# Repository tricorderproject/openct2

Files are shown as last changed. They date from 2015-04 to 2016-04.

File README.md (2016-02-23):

openct2
======

Open Source Computed Tomography (CT) Scanner v2 <br>
http://www.tricorderproject.org/openct <br>
Copyright (C) 2015  Peter Jansen and the Tricorder project <br>
peter@tricorderproject.org <br>
Project Build Logs: https://hackaday.io/project/5946-openct2 <br>

# Introduction

The Open Source Computed Tomography (CT) Scanner project aims to move towards creating an inexpensive and open desktop computed tomography scanner for academic and educational purposes.  The most common form of computed tomography is radiographic using x-rays or gamma rays, although it is my hope that this project can serve as a general platform for other kinds of tomographic research with other, safer wavelengths. 

This project is intended for use with radioisotope "check" sources that are many orders of magnitude less intense than sources in a commercial or medical radiographic setups.  This means that even very low resolution images will take hours of measurement and integration time to assemble, and the resolution and signal to noise ratio of a scan are largely a function of time (and patience).  Much of the spirit of this project is to move towards creating better scans through the use of clever signal processing techniques or wavelengths that can be more efficiently detected, rather than increasing source intensity. 

# Open Source

This project is open hardware and is released under various open licenses.  Please see LICENSES.TXT for details.

For potential contributors, a list of suggested contributions and next steps can be found in TODO.TXT .

# Warning

This project has a variety of dangers associated with it, including (without limitation) its assembly and use.  This generally includes the typical hazards involved with assembling, testing, and using electronics projects, CNC projects, as well as using hand tools, power tools, and CNC manufacturing tools such as laser cutters or CNC routers.  This is not a first project in any of these areas, and one should be well experienced and comfortable in all aspects of this project's design, assembly, and use. 

In addition, for radiography this project makes use of a low intensity sealed radioactive radioisotope source.  You should be experienced and extremely comfortable with handling and using radioactive sources, understanding the potential dangers (and how to minimize them), as well as any local laws or regulations regarding such material.  Having advanced training in medical imaging, radiography, and/or radiation biophysics is highly recommended.  

In no case should any living thing be placed inside of or be scanned by the device. 

**DISCLAIMER OF WARRANTIES AND LIMITATION OF LIABILITY.**

UNLESS OTHERWISE SEPARATELY UNDERTAKEN BY THE LICENSOR, TO THE EXTENT POSSIBLE, THE LICENSOR OFFERS THE LICENSED MATERIAL AS-IS AND AS-AVAILABLE, AND MAKES NO REPRESENTATIONS OR WARRANTIES OF ANY KIND CONCERNING THE LICENSED MATERIAL, WHETHER EXPRESS, IMPLIED, STATUTORY, OR OTHER. THIS INCLUDES, WITHOUT LIMITATION, WARRANTIES OF TITLE, MERCHANTABILITY, FITNESS FOR A PARTICULAR PURPOSE, NON-INFRINGEMENT, ABSENCE OF LATENT OR OTHER DEFECTS, ACCURACY, OR THE PRESENCE OR ABSENCE OF ERRORS, WHETHER OR NOT KNOWN OR DISCOVERABLE. WHERE DISCLAIMERS OF WARRANTIES ARE NOT ALLOWED IN FULL OR IN PART, THIS DISCLAIMER MAY NOT APPLY TO YOU.

TO THE EXTENT POSSIBLE, IN NO EVENT WILL THE LICENSOR BE LIABLE TO YOU ON ANY LEGAL THEORY (INCLUDING, WITHOUT LIMITATION, NEGLIGENCE) OR OTHERWISE FOR ANY DIRECT, SPECIAL, INDIRECT, INCIDENTAL, CONSEQUENTIAL, PUNITIVE, EXEMPLARY, OR OTHER LOSSES, COSTS, EXPENSES, OR DAMAGES ARISING OUT OF THIS PUBLIC LICENSE OR USE OF THE LICENSED MATERIAL, EVEN IF THE LICENSOR HAS BEEN ADVISED OF THE POSSIBILITY OF SUCH LOSSES, COSTS, EXPENSES, OR DAMAGES. WHERE A LIMITATION OF LIABILITY IS NOT ALLOWED IN FULL OR IN PART, THIS LIMITATION MAY NOT APPLY TO YOU.

THE DISCLAIMER OF WARRANTIES AND LIMITATION OF LIABILITY PROVIDED ABOVE SHALL BE INTERPRETED IN A MANNER THAT, TO THE EXTENT POSSIBLE, MOST CLOSELY APPROXIMATES AN ABSOLUTE DISCLAIMER AND WAIVER OF ALL LIABILITY.

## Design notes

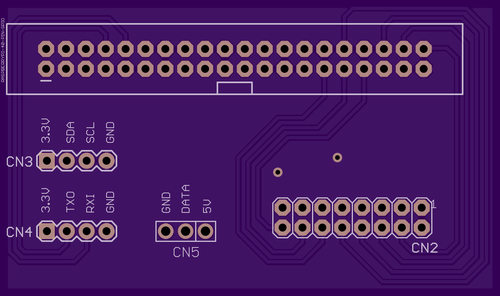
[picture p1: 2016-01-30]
hardware/navscreen/images/navscreen_piboard_rev0_top.png

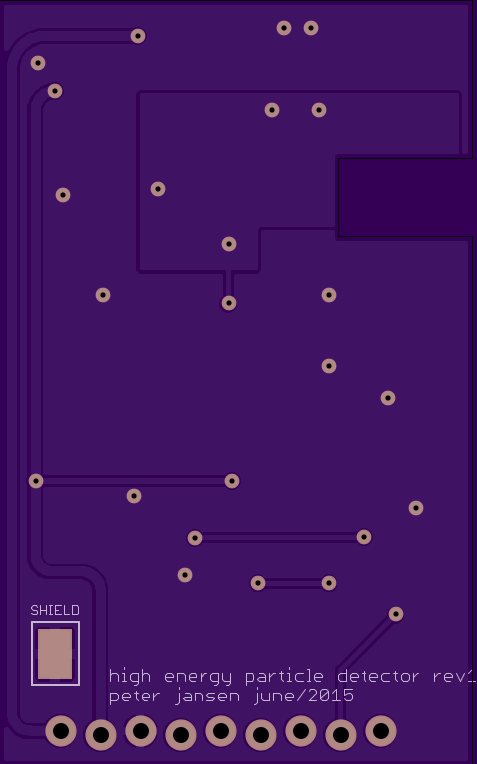
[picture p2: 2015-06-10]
hardware/radiationsensor_r1/images/radiationsensor_r1_bottom.png

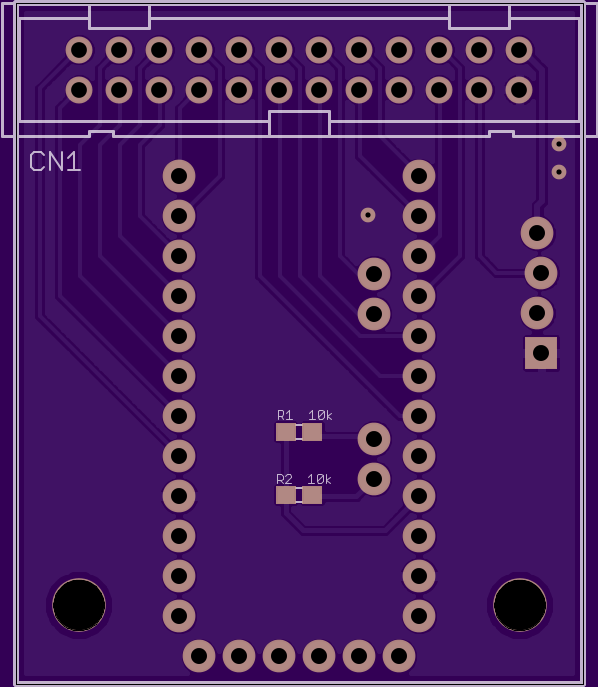
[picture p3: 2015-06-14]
hardware/radiationsensor_r1/images/microcontrollerboard_r0_top.png

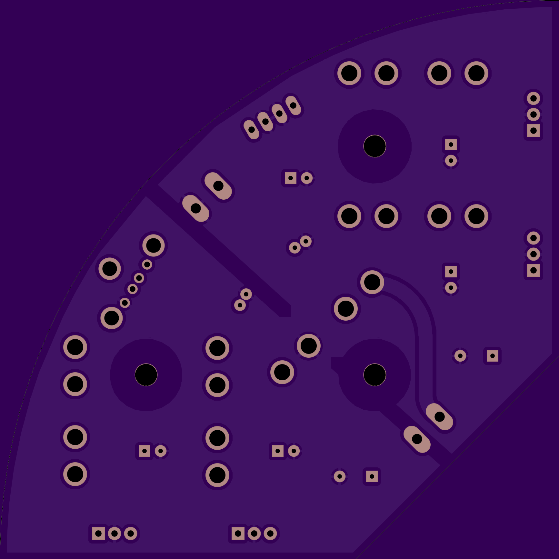
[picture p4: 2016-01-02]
hardware/powersupply/images/powersupply_r0_bottom.png

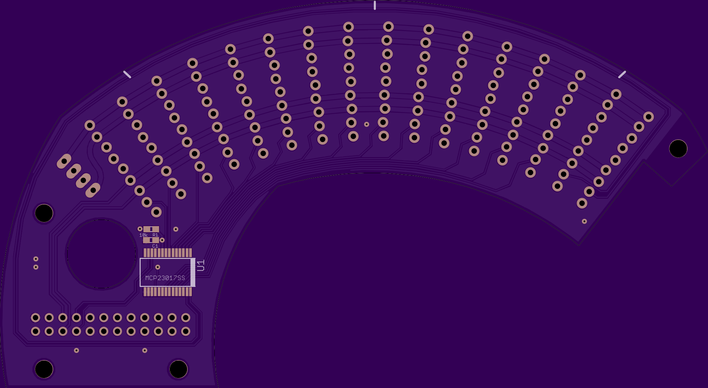
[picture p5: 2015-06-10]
hardware/radiationsensor_r1/images/arrayboard_r0_bottom.png

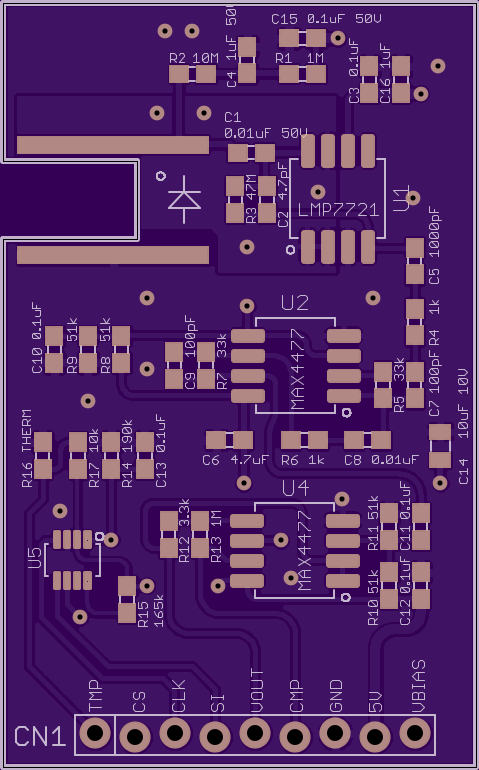
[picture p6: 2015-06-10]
hardware/radiationsensor_r1/images/radiationsensor_r1_top.png

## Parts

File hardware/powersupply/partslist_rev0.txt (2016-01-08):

CN1, CN3	JST Connector	B2B-PH-K-S(LF)(SN)
+ Cables (from Sparkfun?)

CN2		USB Connector	Molex 105057-0001		

CN4		Imaging Array Connector		A33896-ND

CN5, CN6	5mm pitch Screw Terminals			1776244-2

C3-C6		Capacitors	5mm dia, 47uF, 16V	(ECA-1EHG470)
C7		Capacitor	5mm dia, 100V		(ECA-2AM100)
C1-C2		Capacitors	10mm dia, 25V 		(ECA-1VM471)

IC1-4		2A Linear Regulators	L78S05CV-DG

F1-5		20mm/5mm Fuse Clips (qty 10)	1A3399-10

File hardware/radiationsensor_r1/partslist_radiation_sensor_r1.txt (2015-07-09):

Partlist											
											
Part	Value	Device	Package		QTY per board		# of boards		QTY total		Digikey #
											
C1	0.01uF	50V	CAP0603		1		18		18		445-16165-1-ND
"C10, *"	0.1uF	50V	603		6		18		108		311-1344-1-ND
C5	1000pF	CAP0603	603		1		18		18		445-5736-1-ND
"C7, C9"	100pF	CAP0603	603		2		18		36		1276-2159-1-ND
C14	10uF	10V	805		1		18		18		490-3886-1-ND
"C4, C16"	1uF	50V	603		2		18		36		445-7468-1-ND
C2	2.2pF	50V	603		1		18		18		399-8791-1-ND
C6	4.7uF	CAP0603	603		1		18		18		1276-1784-1-ND
											
CN1	1X09	MALE RIGHTANGLE	1X09		1		18		18		S1111EC-09-ND
											
D1	BPW34S	PHOTODIODE4STACK-SIDEMOUNT	BPW34S-4STACK-SIDEMOUNT		4		18		72		BPW34S-ND
											
R17	10k	RESISTOR0603	603		1		18		18		P10.0KHCT-ND
R2	10M	RESISTOR0603	603		1		18		18		541-10MAYCT-ND
R15	165k	RESISTOR0603	603		1		18		18		P165KHCT-ND
R14	190k	RESISTOR0603	603		1		18		18		P191KHCT-ND
"R4, R6"	1k	RESISTOR0603	603		2		18		36		P1.00KHCT-ND
"R1, R13"	1M	RESISTOR0603	603		2		18		36		P1.00MHCT-ND
R12	3.3k	RESISTOR0603	603		1		18		18		P3.30KHCT-ND
"R5, R7"	33k	RESISTOR0603	603		2		18		36		P33.0KHCT-ND
R3	47M	RESISTOR0603	603		1		18		18		541-47MAHCT-ND
"R10, R9, R10, R11"	51k	RESISTOR0603	603		4		18		72		P51.0KHCT-ND
R16	NCP18XV103	RESISTOR0603	603		1		18		18		490-6944-1-ND
											
U1	LMP7721	OPAMP-LMP7721	SOIC-8		1		18		18		LMP7721MA/NOPB-ND
"U2, U4"	MAX4477	OPAMP-MAX4477	SOIC-8		2		18		36		MAX4477ASA+-ND
U5	50k	AD5160	SOT-23-8		1		18		18		AD5160BRJZ50-RL7CT-ND
											
Other											
Stranded Wire for Ground Shield					1		1		1		CN100B-25-ND
Roll of Aluminum Tape											Hardware Store

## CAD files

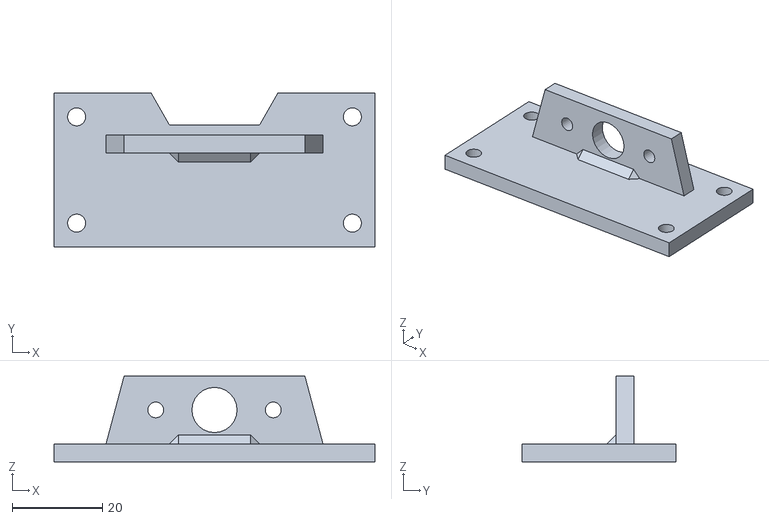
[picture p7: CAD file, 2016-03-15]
mechanical/structure/shield_mount1a_fixed.stl
71.0 x 34.0 x 19.0

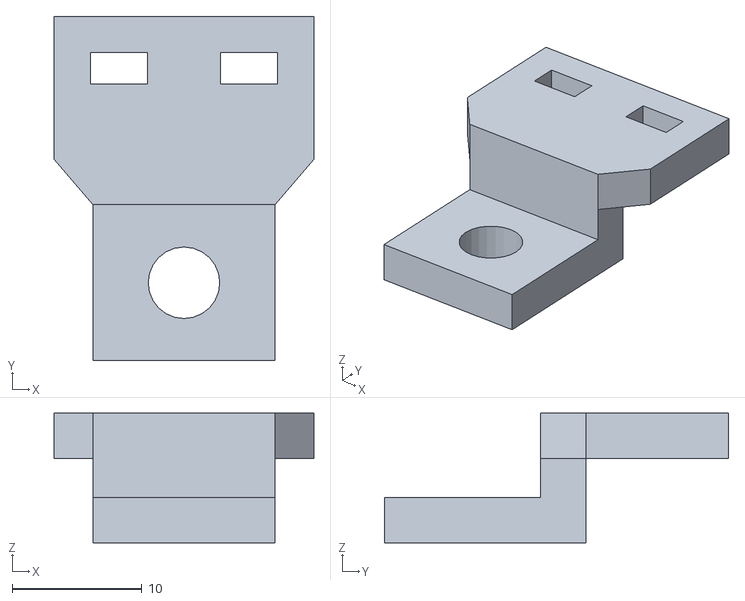
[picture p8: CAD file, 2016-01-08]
mechanical/structure/limitswitch_mount1a_fixed.stl
20.0 x 26.5 x 10.00

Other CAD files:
mechanical/structure/limitswitch_mount1a.skp
mechanical/structure/notes_nutholder2a2.skp
mechanical/structure/shield_mount1a.skp

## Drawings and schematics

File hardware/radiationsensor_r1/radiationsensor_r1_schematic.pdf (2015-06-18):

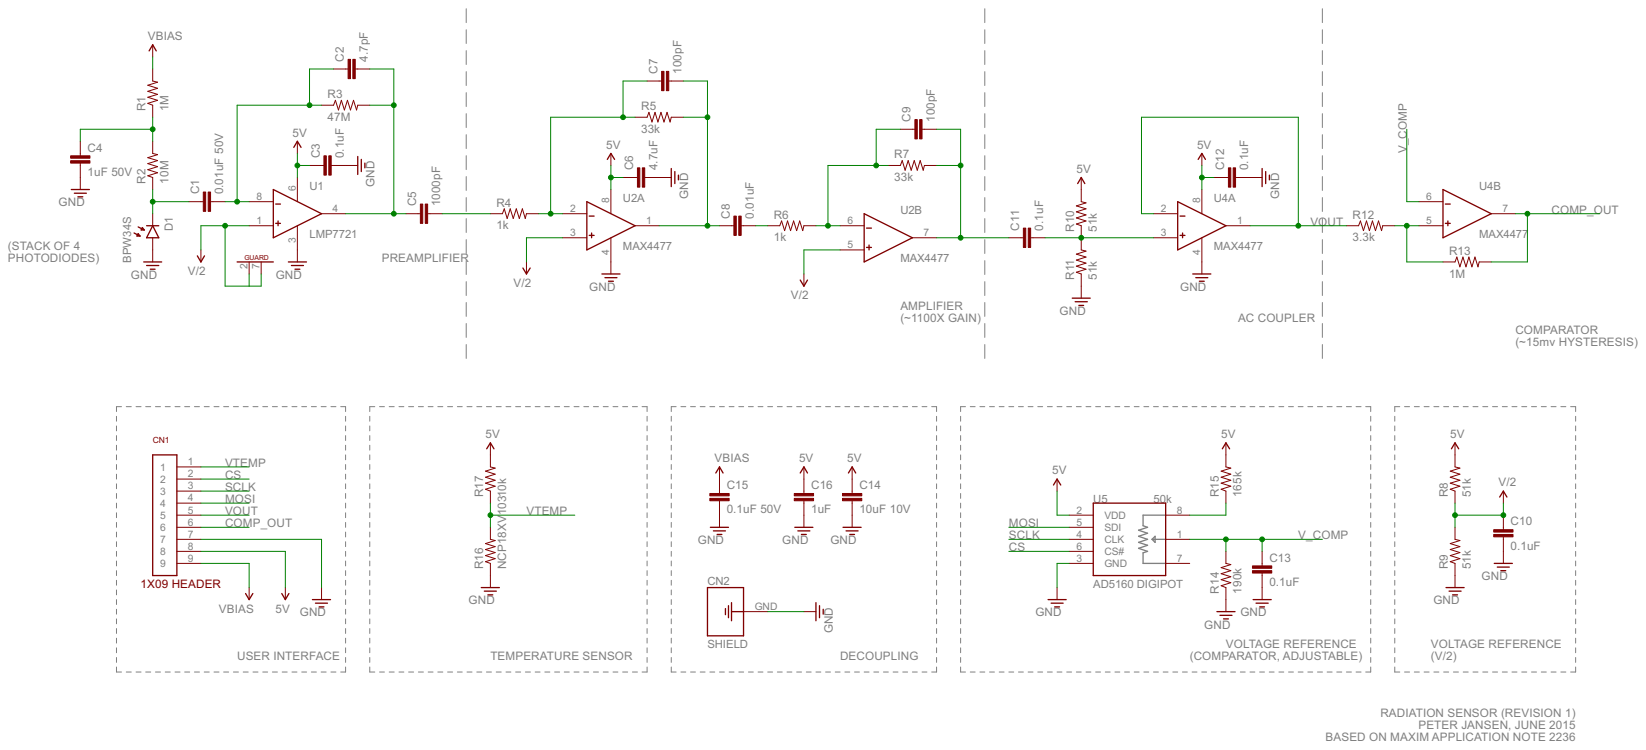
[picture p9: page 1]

PETER JANSEN, JUNE 2015 RADIATION SENSOR (REVISION 1) BASED ON MAXIM APPLICATION NOTE 2236

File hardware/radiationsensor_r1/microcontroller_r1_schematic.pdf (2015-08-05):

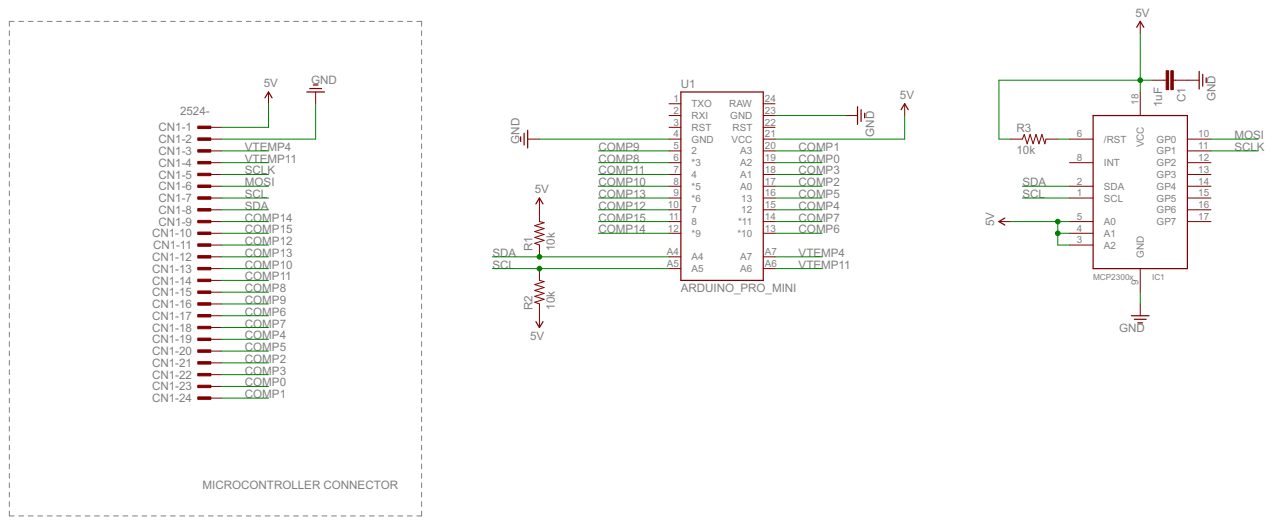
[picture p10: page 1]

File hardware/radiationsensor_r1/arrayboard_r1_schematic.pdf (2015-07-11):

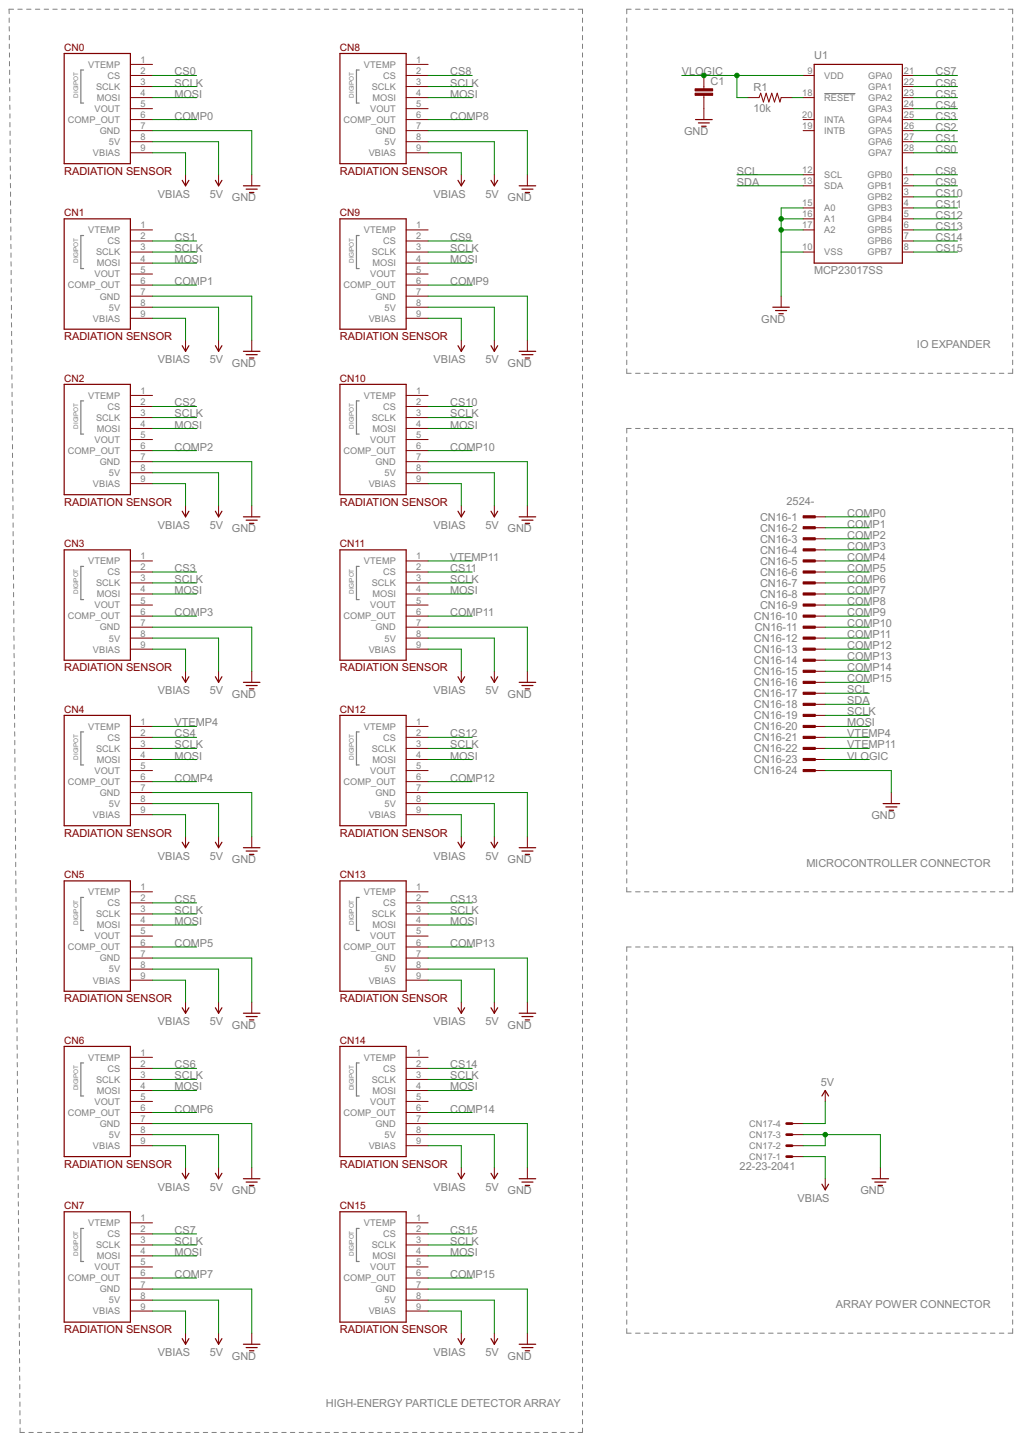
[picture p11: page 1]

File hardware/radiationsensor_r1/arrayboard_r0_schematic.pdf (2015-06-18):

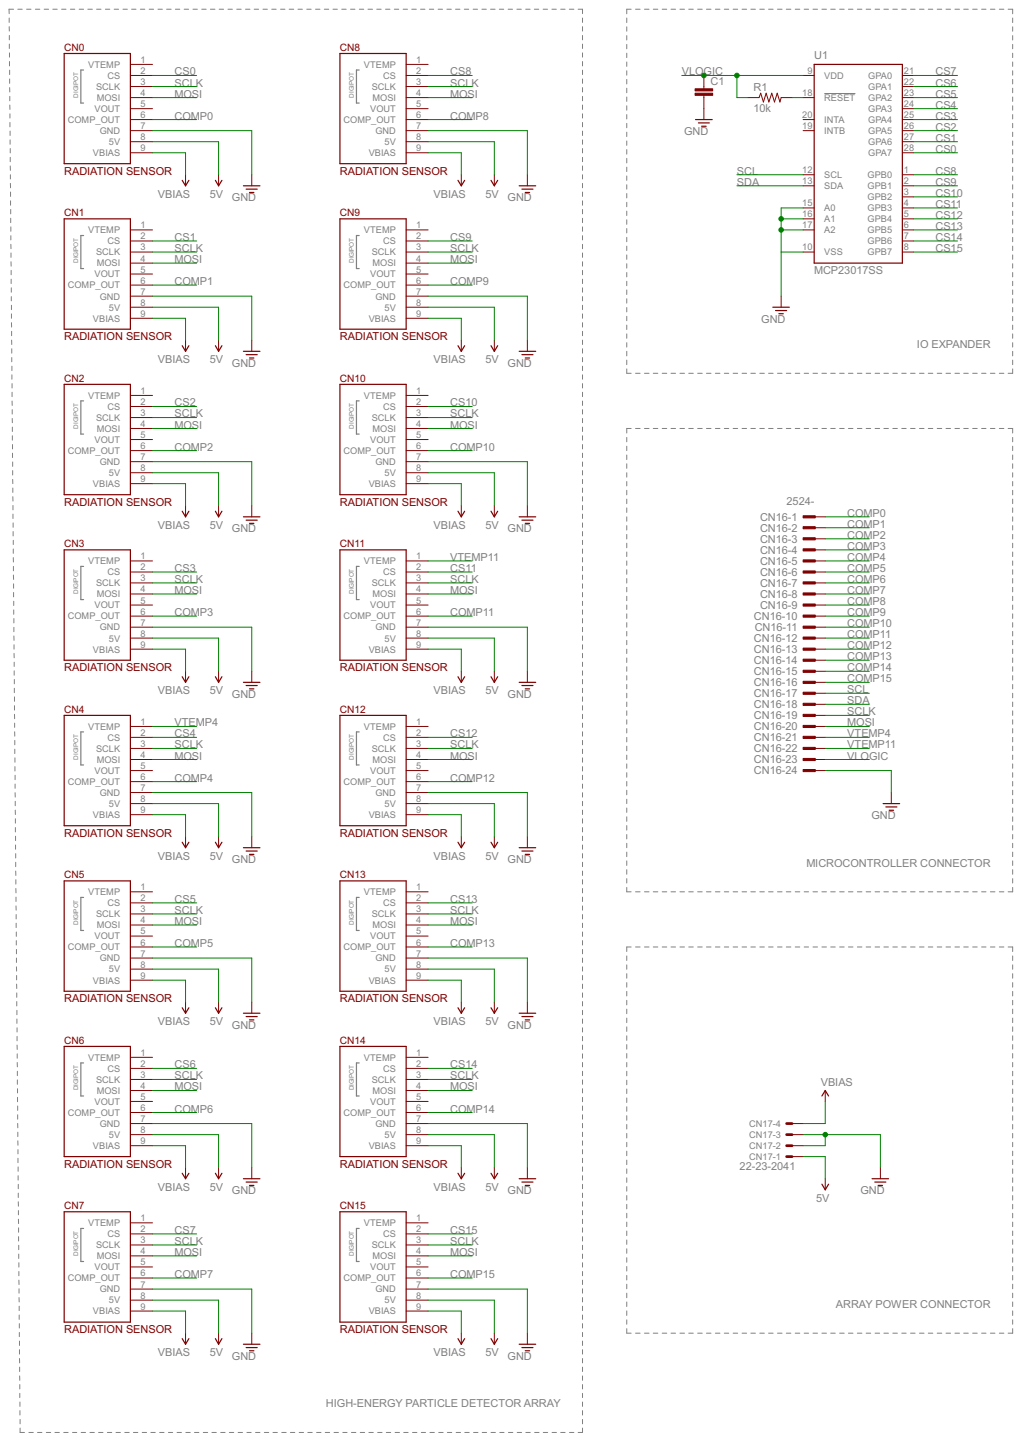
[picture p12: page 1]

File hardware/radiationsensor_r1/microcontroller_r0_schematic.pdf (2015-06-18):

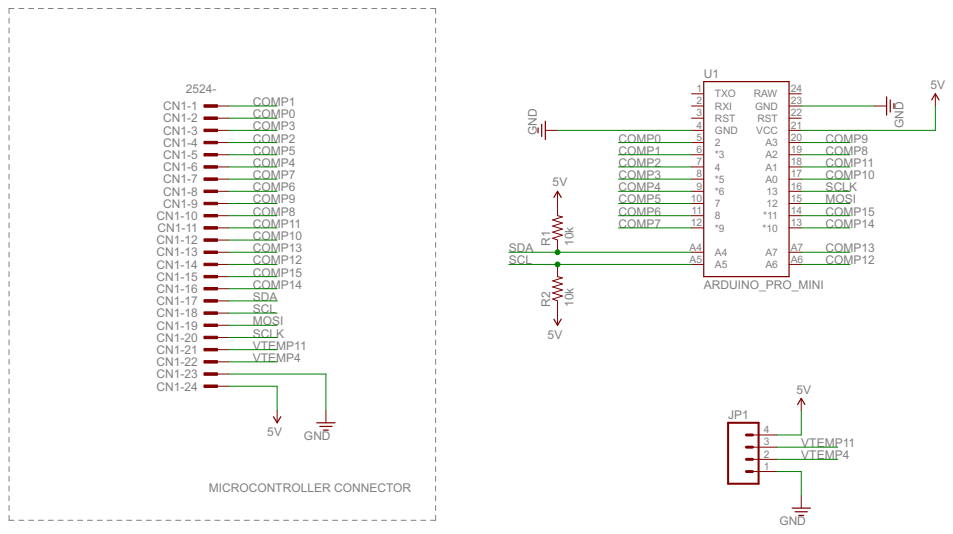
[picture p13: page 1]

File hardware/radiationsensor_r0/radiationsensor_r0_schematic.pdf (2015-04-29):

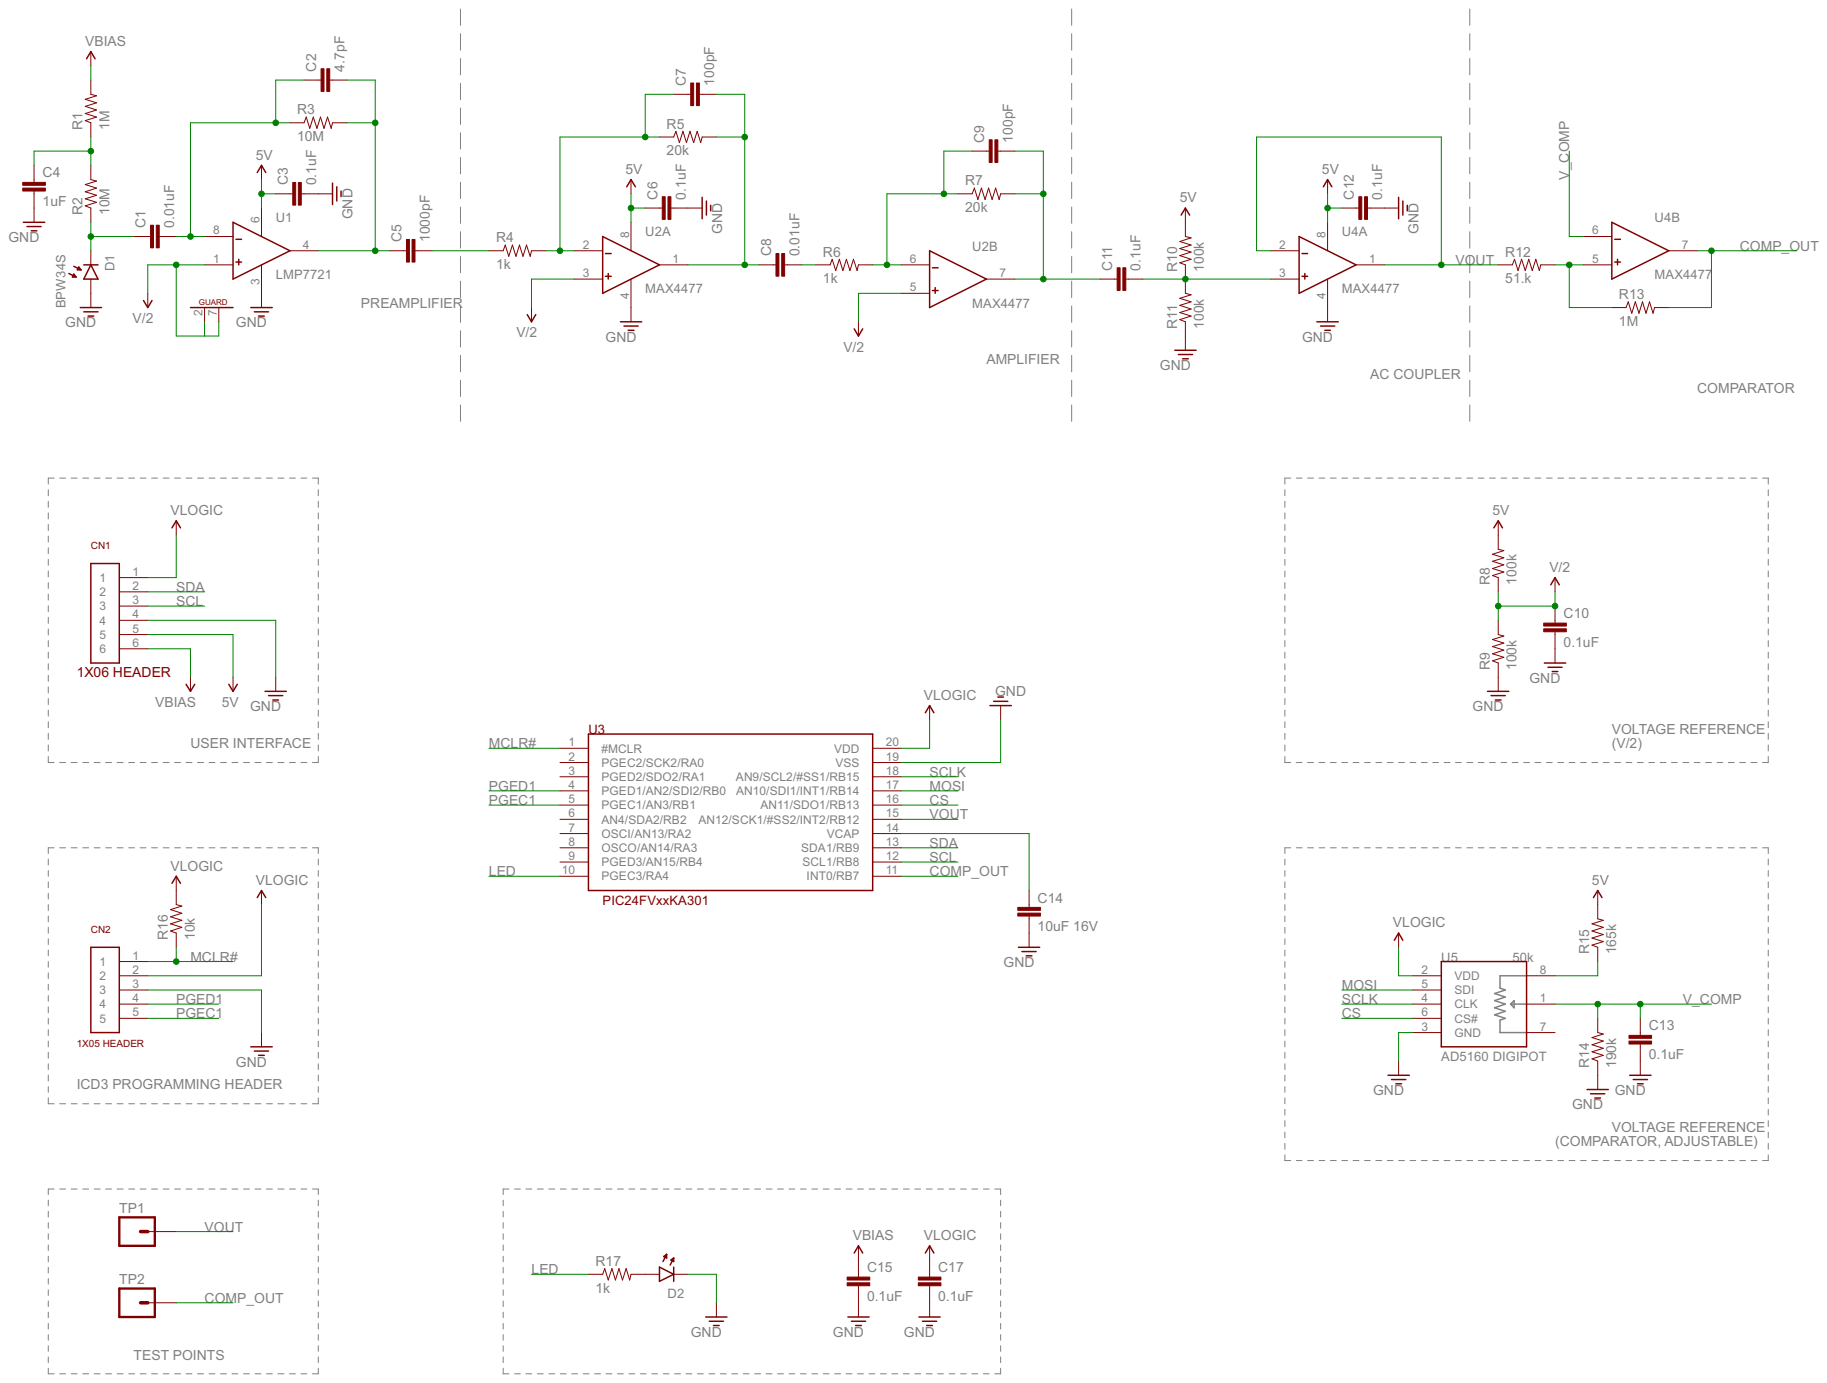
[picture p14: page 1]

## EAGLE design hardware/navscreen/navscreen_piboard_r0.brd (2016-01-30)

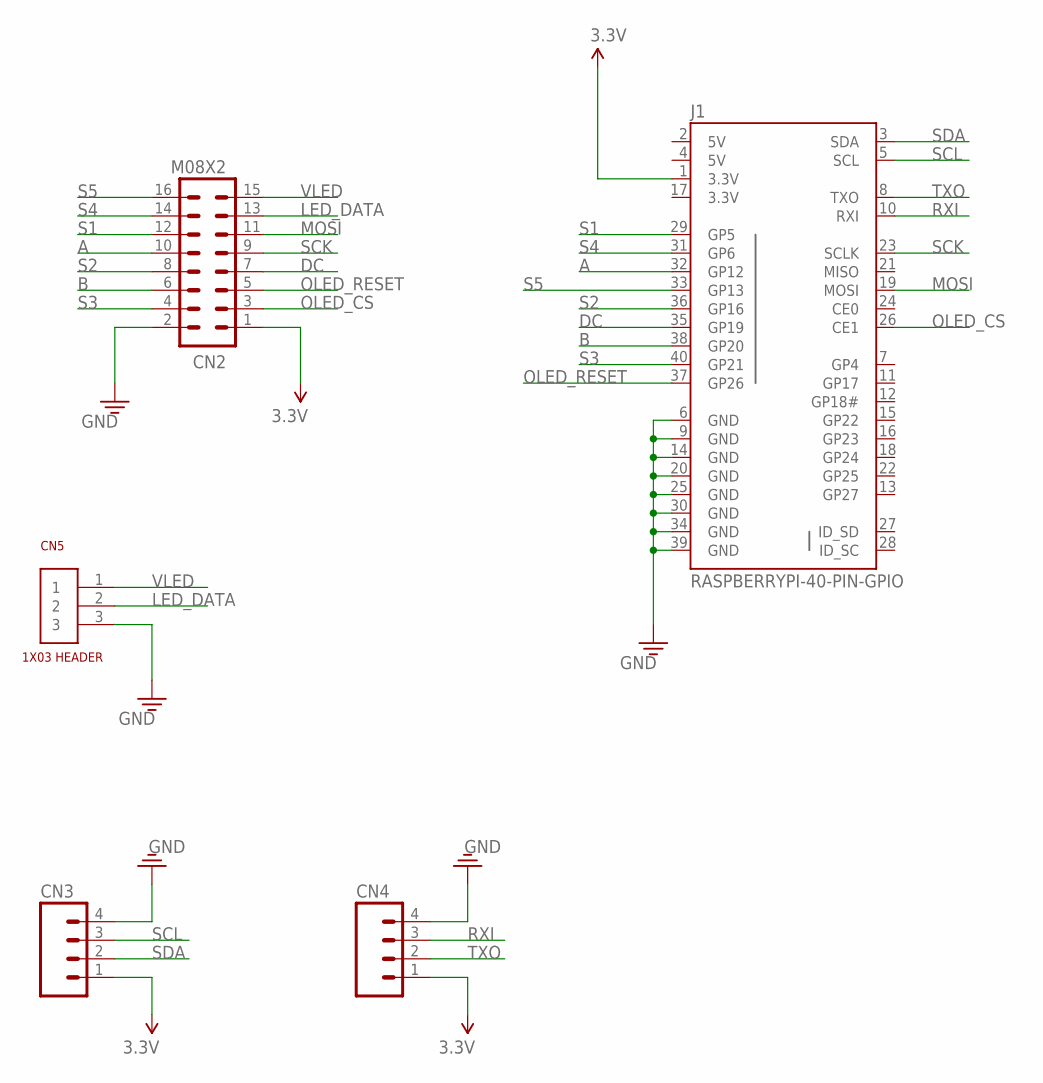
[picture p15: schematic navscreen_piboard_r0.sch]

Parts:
CN2: M08X2; 2X8
CN3, CN4: M04PTH; 1X04
CN5: 1X03
J1: RASPBERRYPI-40-PIN-GPIO; 2X20-SHROUDED

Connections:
3.3V: CN2.1, CN3.1, CN4.1, J1.1 (3.3V), J1.17 (3.3V)
A: CN2.10, J1.32 (GP12)
B: CN2.6, J1.38 (GP20)
DC: CN2.7, J1.35 (GP19)
GND: CN2.2, CN3.4, CN4.4, CN5.3, J1.6 (GND), J1.9 (GND), J1.14 (GND), J1.20 (GND), J1.25 (GND), J1.30 (GND), J1.34 (GND), J1.39 (GND)
LED_DATA: CN2.13, CN5.2
MOSI: CN2.11, J1.19 (MOSI)
OLED_CS: CN2.3, J1.26 (CE1)
OLED_RESET: CN2.5, J1.37 (GP26)
RXI: CN4.3, J1.10 (RXI)
S1: CN2.12, J1.29 (GP5)
S2: CN2.8, J1.36 (GP16)
S3: CN2.4, J1.40 (GP21)
S4: CN2.14, J1.31 (GP6)
S5: CN2.16, J1.33 (GP13)
SCK: CN2.9, J1.23 (SCLK)
SCL: CN3.3, J1.5 (SCL)
SDA: CN3.2, J1.3 (SDA)
TXO: CN4.2, J1.8 (TXO)
VLED: CN2.15, CN5.1, J1.2 (5V), J1.4 (5V)

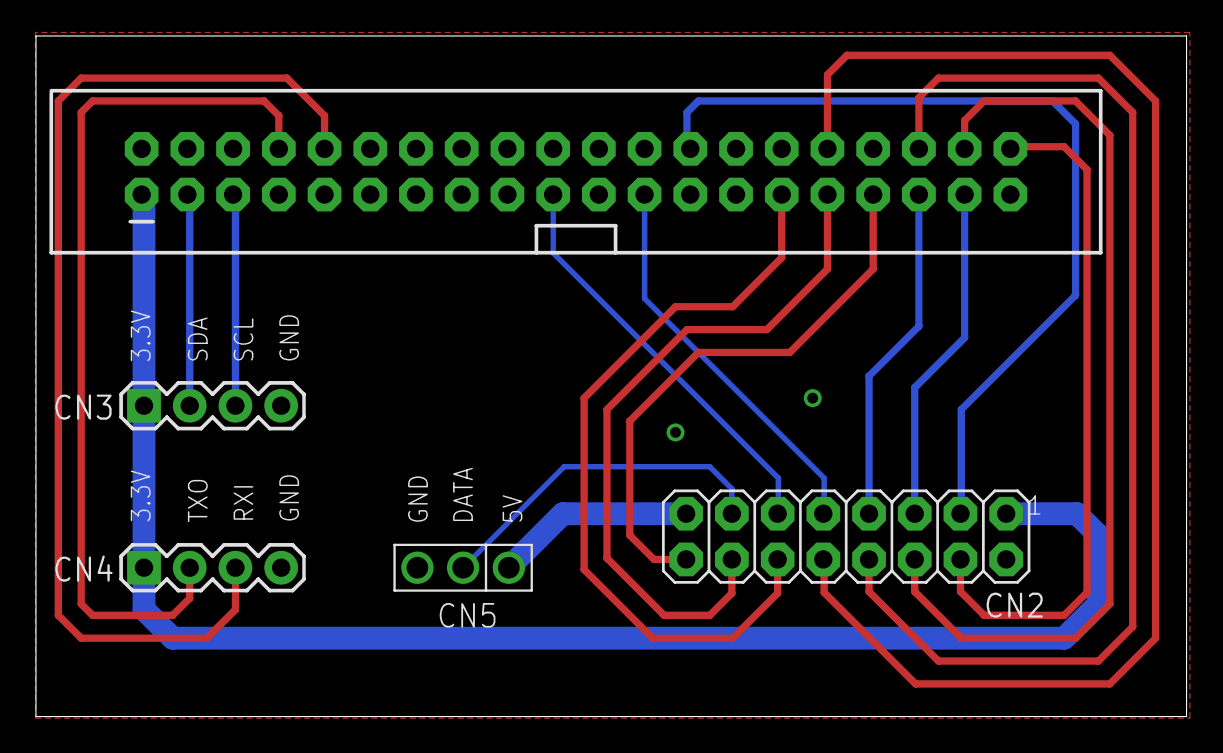
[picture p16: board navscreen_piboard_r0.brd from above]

Board: 2 copper layers, 63.9 x 37.8 mm, 5 parts (0 on the bottom side), 20 nets.

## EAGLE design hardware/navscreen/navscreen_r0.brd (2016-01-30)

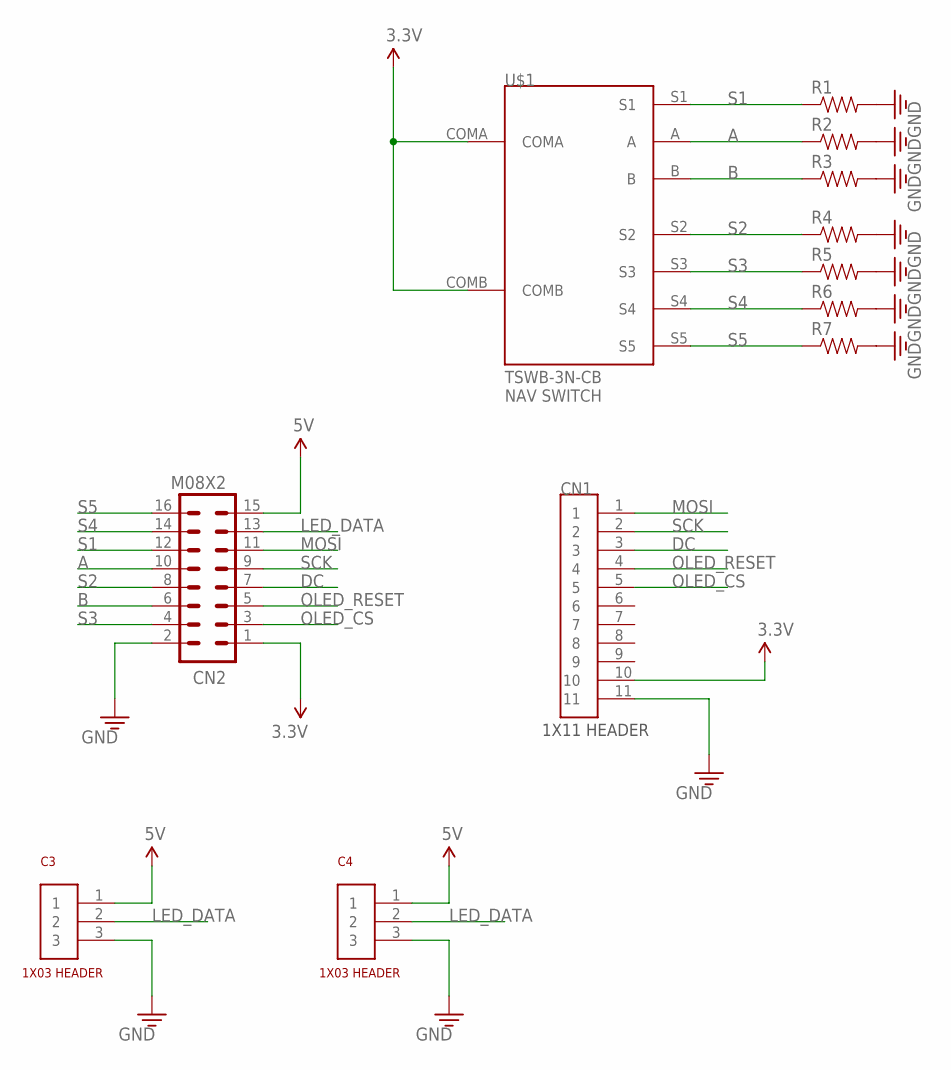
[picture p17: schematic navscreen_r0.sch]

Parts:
C3, C4: 1X03
CN1: 1X11
CN2: M08X2; 2X8
R1, R2, R3, R4, R5, R6, R7: RESISTOR0603; 0603
U$1: NAV-SWITCH-TSWB-3N-CB; TSWB-3N-CB

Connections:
3.3V: CN1.10, CN2.1, U$1.COMA, U$1.COMB
5V: C3.1, C4.1, CN2.15
A: CN2.10, R2.1, U$1.A
B: CN2.6, R3.1, U$1.B
DC: CN1.3, CN2.7
GND: C3.3, C4.3, CN1.11, CN2.2, R1.2, R2.2, R3.2, R4.2, R5.2, R6.2, R7.2
LED_DATA: C3.2, C4.2, CN2.13
MOSI: CN1.1, CN2.11
OLED_CS: CN1.5, CN2.3
OLED_RESET: CN1.4, CN2.5
S1: CN2.12, R1.1, U$1.S1
S2: CN2.8, R4.1, U$1.S2
S3: CN2.4, R5.1, U$1.S3
S4: CN2.14, R6.1, U$1.S4
S5: CN2.16, R7.1, U$1.S5
SCK: CN1.2, CN2.9

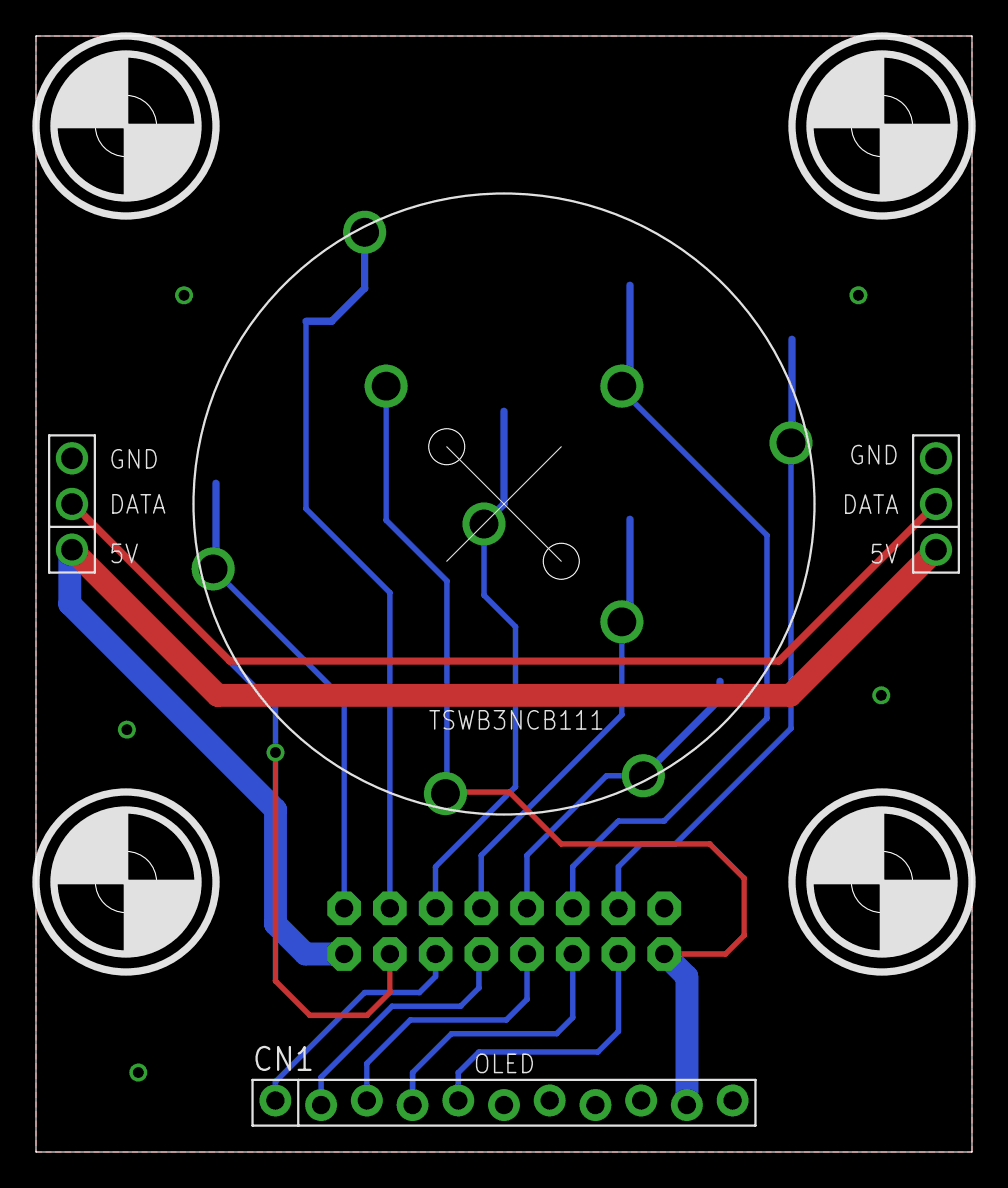
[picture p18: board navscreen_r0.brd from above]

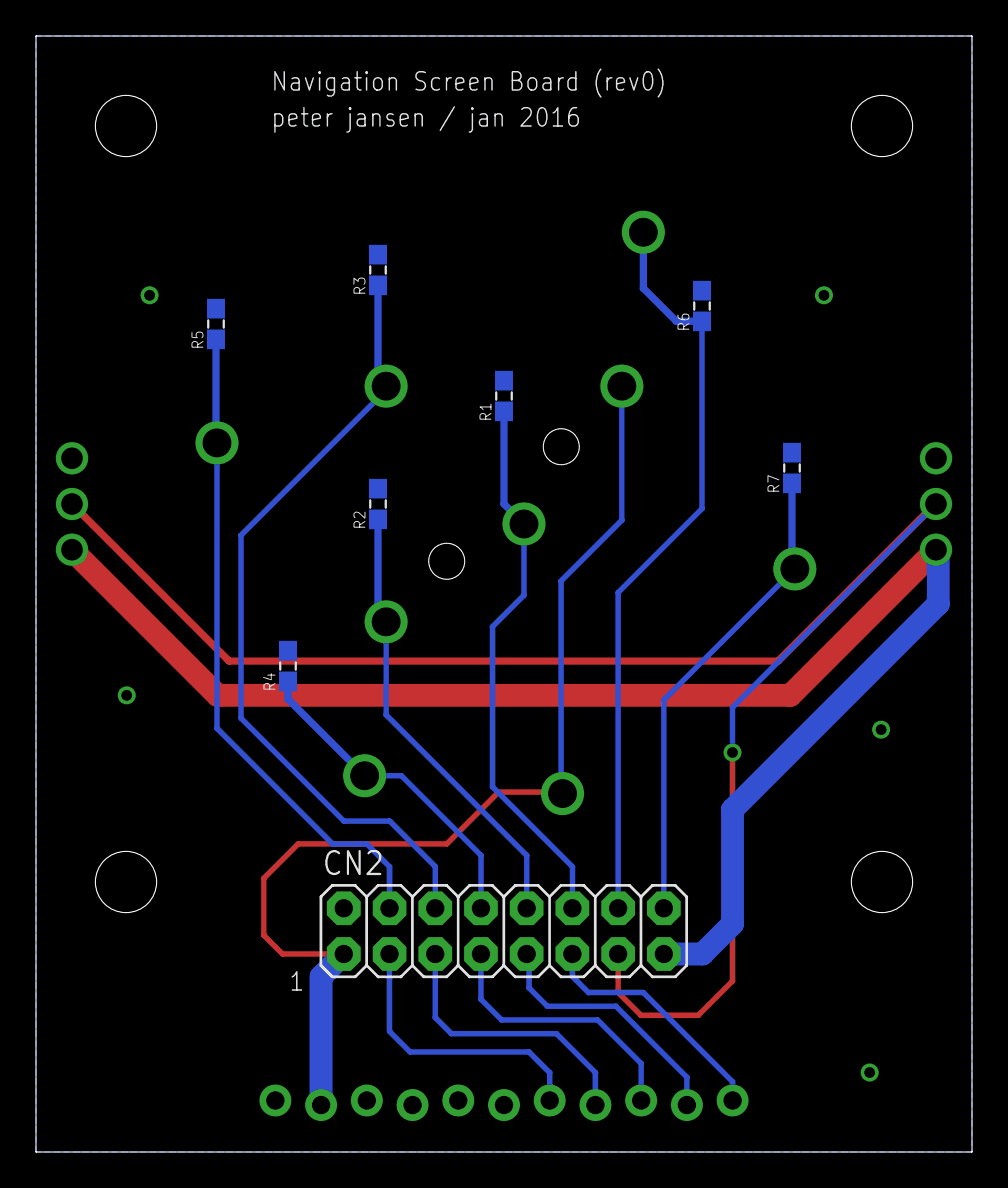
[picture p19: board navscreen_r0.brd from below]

Board: 2 copper layers, 52.0 x 62.0 mm, 12 parts (8 on the bottom side), 16 nets.

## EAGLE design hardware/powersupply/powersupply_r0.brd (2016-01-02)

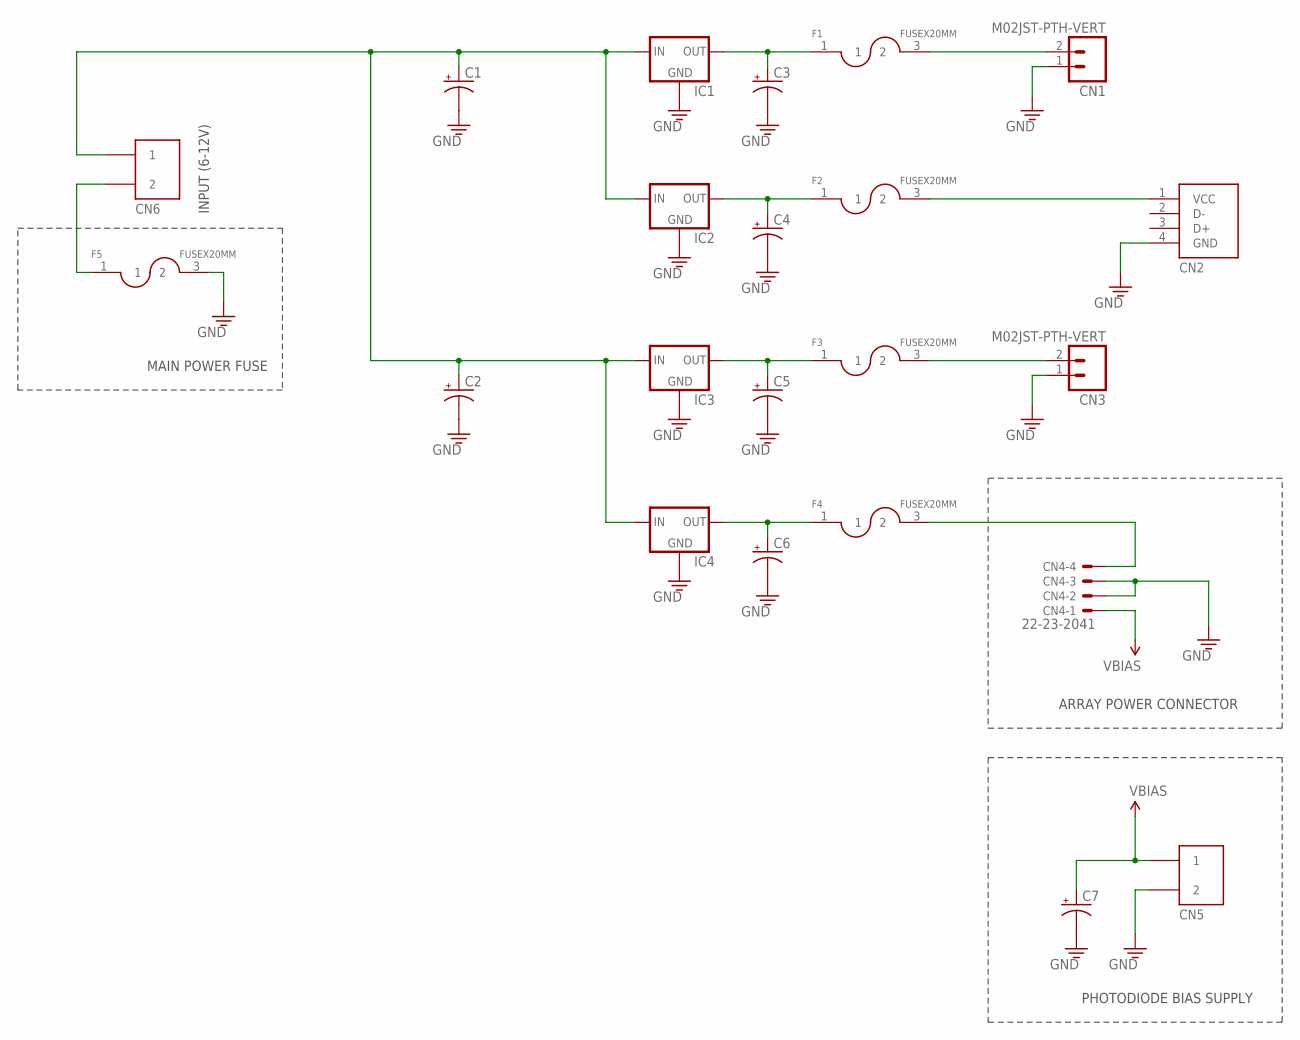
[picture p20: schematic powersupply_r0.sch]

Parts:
C1, C2: CAP_POLPTH4; CPOL-RADIAL-1000UF-25V
C3, C4, C5, C6, C7: CAP_POLPTH1; CPOL-RADIAL-100UF-25V
CN1, CN3: M02JST-PTH-VERT; JST-2-PTH-VERT
CN2: CON-USB; MOLEX-USB-105057-0001
CN4: 22-23-2041
CN5, CN6: SCREWTERMINAL-2PIN
F1, F2, F3, F4, F5: FUSEX20MM; FUSE_5MM
IC1, IC2, IC3, IC4: V_REG_78XXSINK; TO220-IGO

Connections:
GND: C1.2 (-), C2.2 (-), C3.2 (-), C4.2 (-), C5.2 (-), C6.2 (-), C7.2 (-), CN1.1 (2), CN2.4 (GND), CN3.1 (2), CN4.2, CN4.3, CN5.2, F5.3 (2), IC1.GND, IC2.GND, IC3.GND, IC4.GND
unnamed: C3.1 (+), F1.1, IC1.OUT
unnamed: C4.1 (+), F2.1, IC2.OUT
unnamed: C5.1 (+), F3.1, IC3.OUT
unnamed: C6.1 (+), F4.1, IC4.OUT
unnamed: CN4.4, F4.3 (2)
unnamed: CN6.2, F5.1
unnamed: CN1.2 (1), F1.3 (2)
unnamed: CN2.1 (VCC), F2.3 (2)
unnamed: CN3.2 (1), F3.3 (2)
unnamed: C1.1 (+), C2.1 (+), CN6.1, IC1.IN, IC2.IN, IC3.IN, IC4.IN
VBIAS: C7.1 (+), CN4.1, CN5.1

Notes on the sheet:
ARRAY POWER CONNECTOR
MAIN POWER FUSE
INPUT (6-12V)
PHOTODIODE BIAS SUPPLY

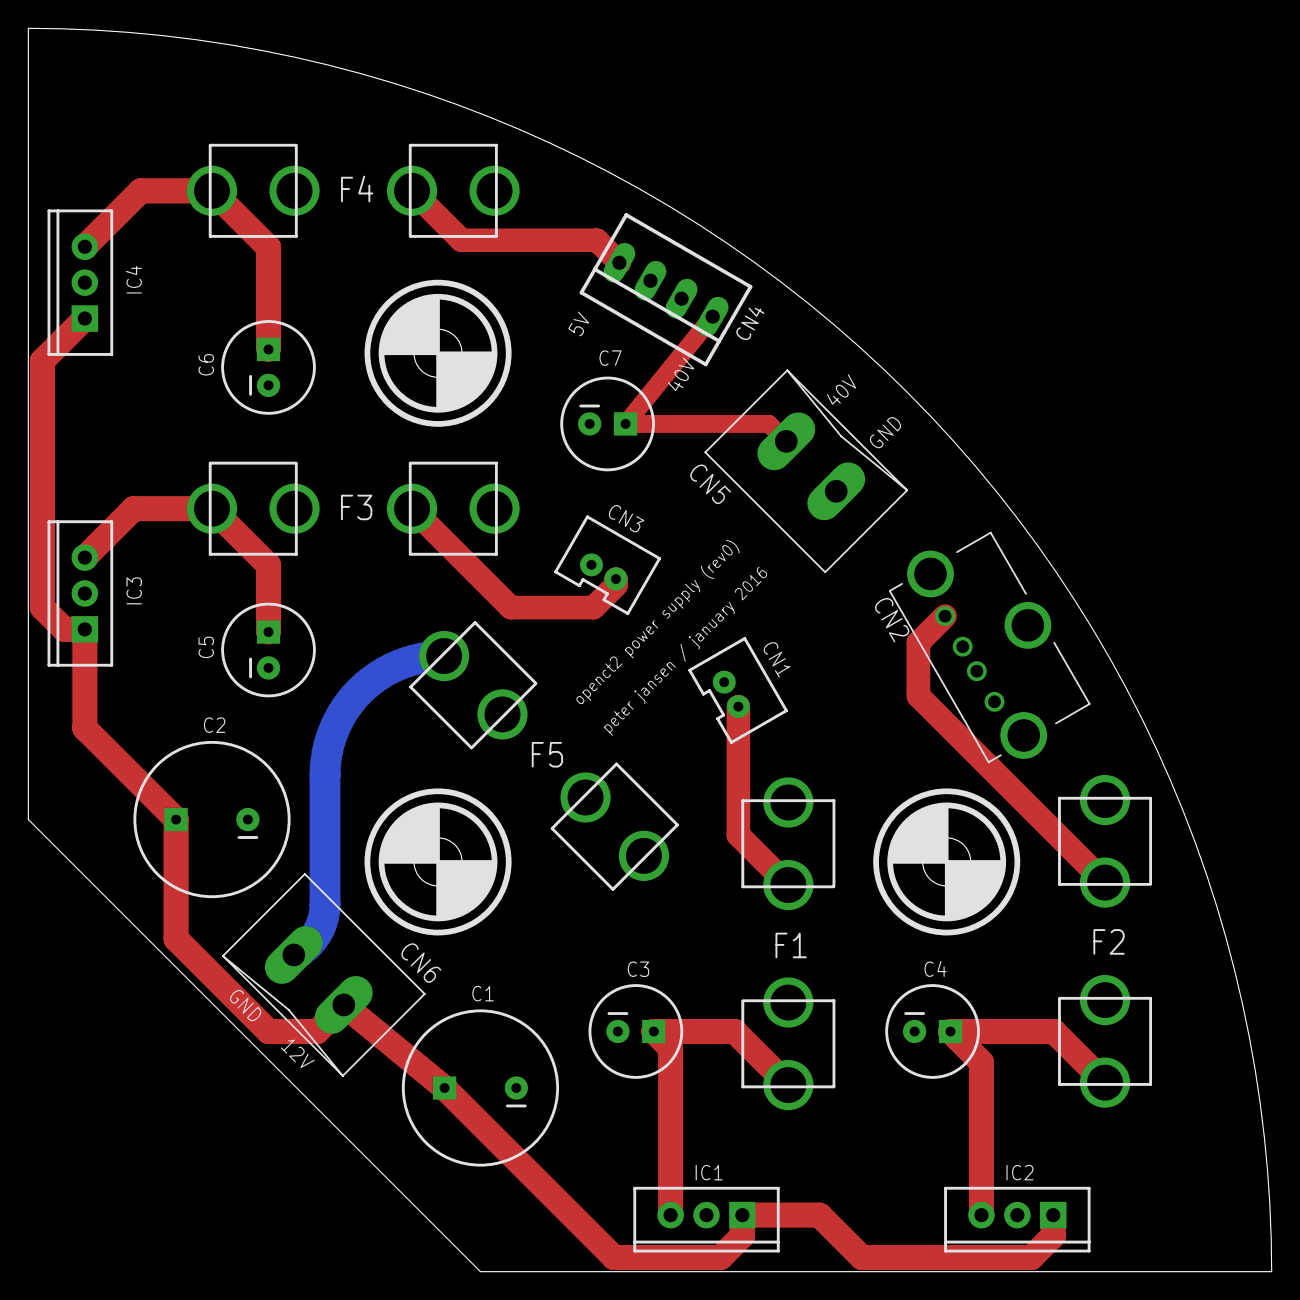
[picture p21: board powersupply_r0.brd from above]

Board: 2 copper layers, 88.0 x 88.0 mm, 22 parts (0 on the bottom side), 12 nets.

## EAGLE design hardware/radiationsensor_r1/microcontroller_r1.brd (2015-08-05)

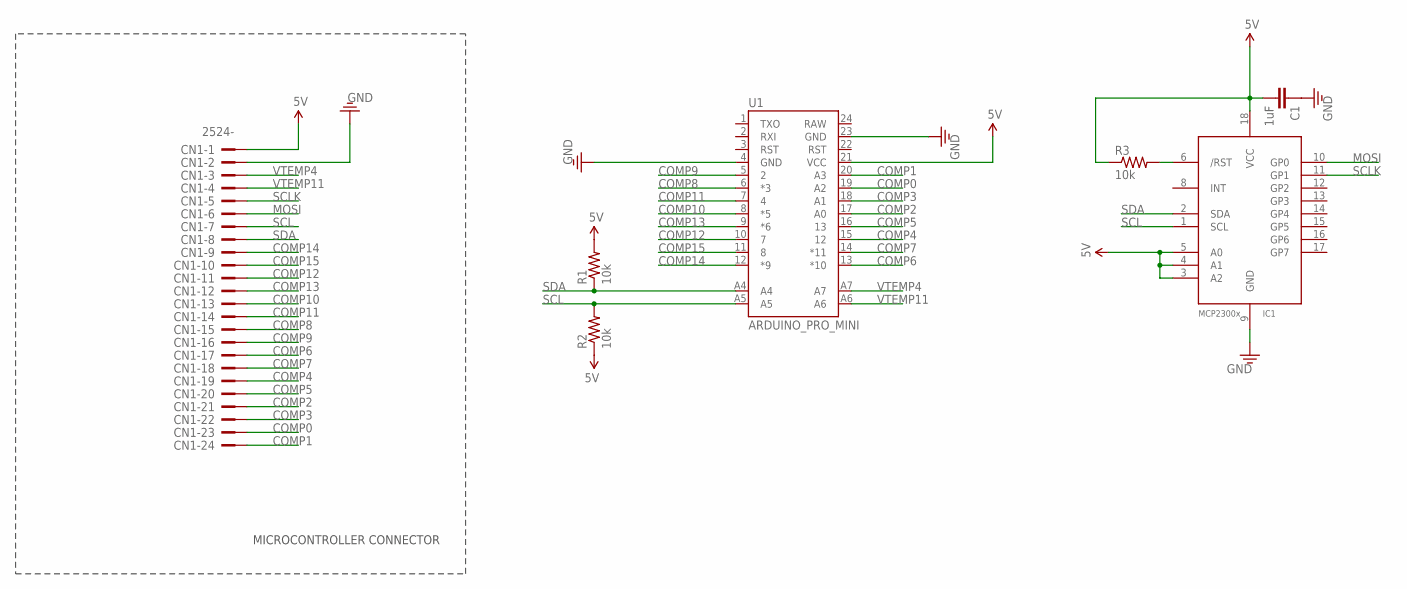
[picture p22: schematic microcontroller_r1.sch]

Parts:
C1: 1uF; 0603
CN1: 2524-; PAK100/2500-24
IC1: MCP2300X/SO; SO18W
R1, R2, R3: 10k; 0603
U1: ARDUINO_PRO_MINI

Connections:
5V: C1.2, CN1.1, IC1.3 (A2), IC1.4 (A1), IC1.5 (A0), IC1.18 (VCC), R1.2, R2.1, R3.1, U1.21 (VCC)
COMP0: CN1.23, U1.19 (A2)
COMP1: CN1.24, U1.20 (A3)
COMP2: CN1.21, U1.17 (A0)
COMP3: CN1.22, U1.18 (A1)
COMP4: CN1.19, U1.15 (12)
COMP5: CN1.20, U1.16 (13)
COMP6: CN1.17, U1.13 (*10)
COMP7: CN1.18, U1.14 (*11)
COMP8: CN1.15, U1.6 (*3)
COMP9: CN1.16, U1.5 (2)
COMP10: CN1.13, U1.8 (*5)
COMP11: CN1.14, U1.7 (4)
COMP12: CN1.11, U1.10 (7)
COMP13: CN1.12, U1.9 (*6)
COMP14: CN1.9, U1.12 (*9)
COMP15: CN1.10, U1.11 (8)
GND: C1.1, CN1.2, IC1.9 (GND), U1.4 (GND), U1.23 (GND)
MOSI: CN1.6, IC1.10 (GP0)
unnamed: IC1.6 (/RST), R3.2
SCL: CN1.7, IC1.1 (SCL), R2.2, U1.A5
SCLK: CN1.5, IC1.11 (GP1)
SDA: CN1.8, IC1.2 (SDA), R1.1, U1.A4
VTEMP4: CN1.3, U1.A7
VTEMP11: CN1.4, U1.A6

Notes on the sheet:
MICROCONTROLLER CONNECTOR

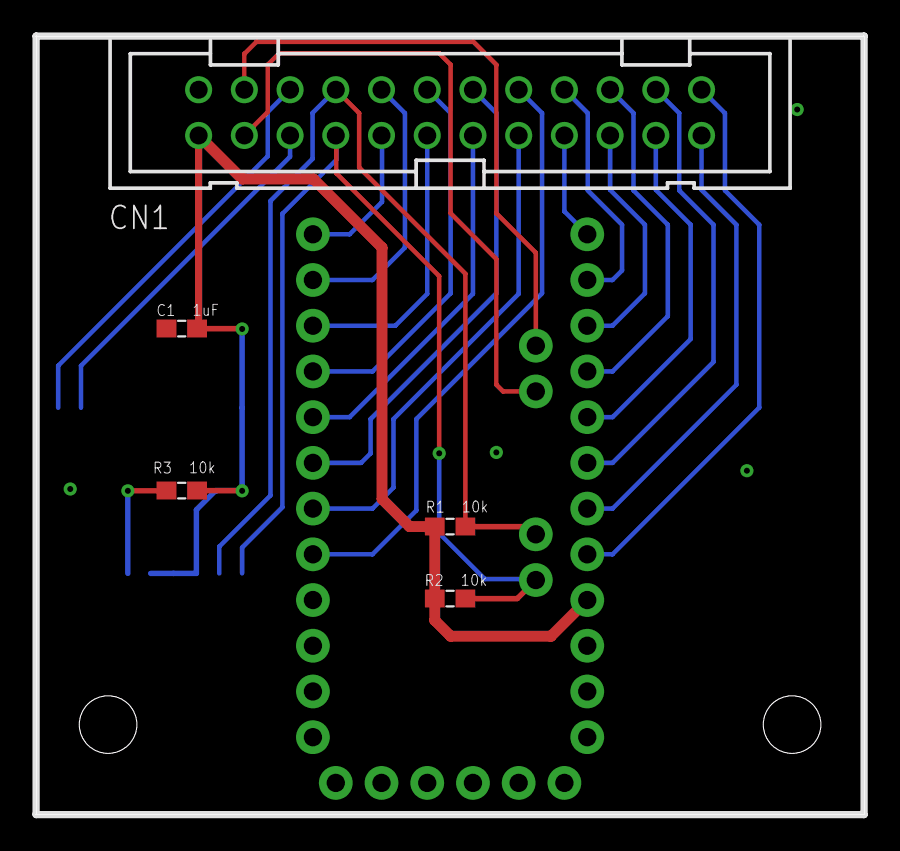
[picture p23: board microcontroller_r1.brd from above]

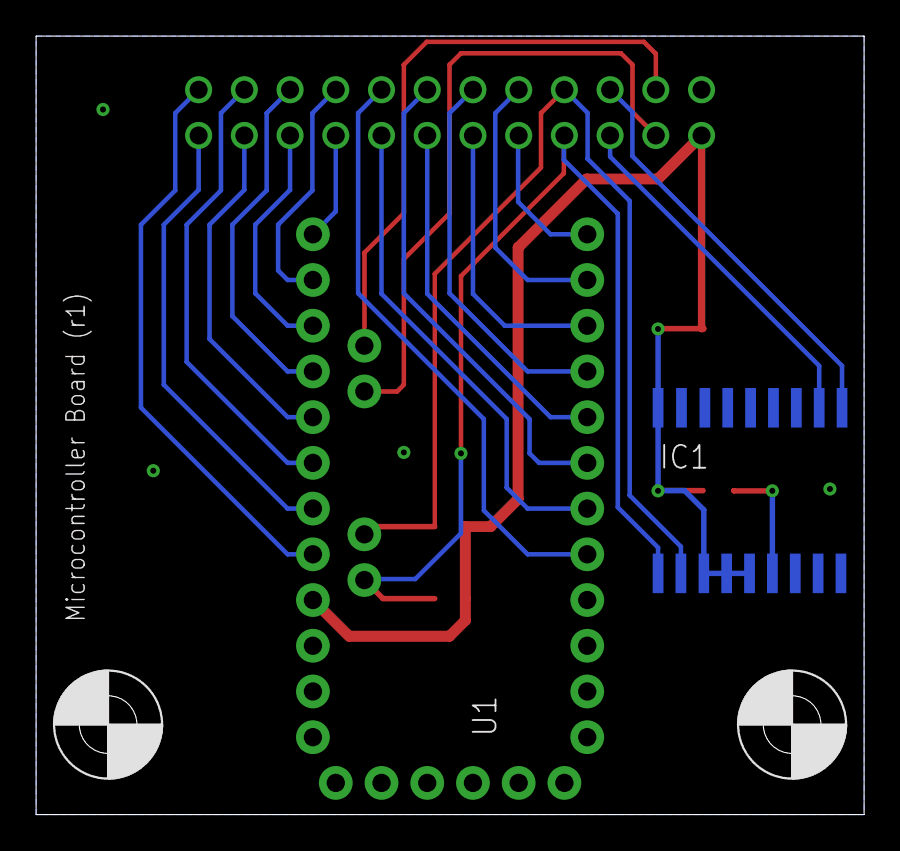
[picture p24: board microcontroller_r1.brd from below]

Board: 2 copper layers, 46.0 x 43.2 mm, 9 parts (4 on the bottom side), 25 nets.

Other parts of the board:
U$35, U$36: MOUNT-M3

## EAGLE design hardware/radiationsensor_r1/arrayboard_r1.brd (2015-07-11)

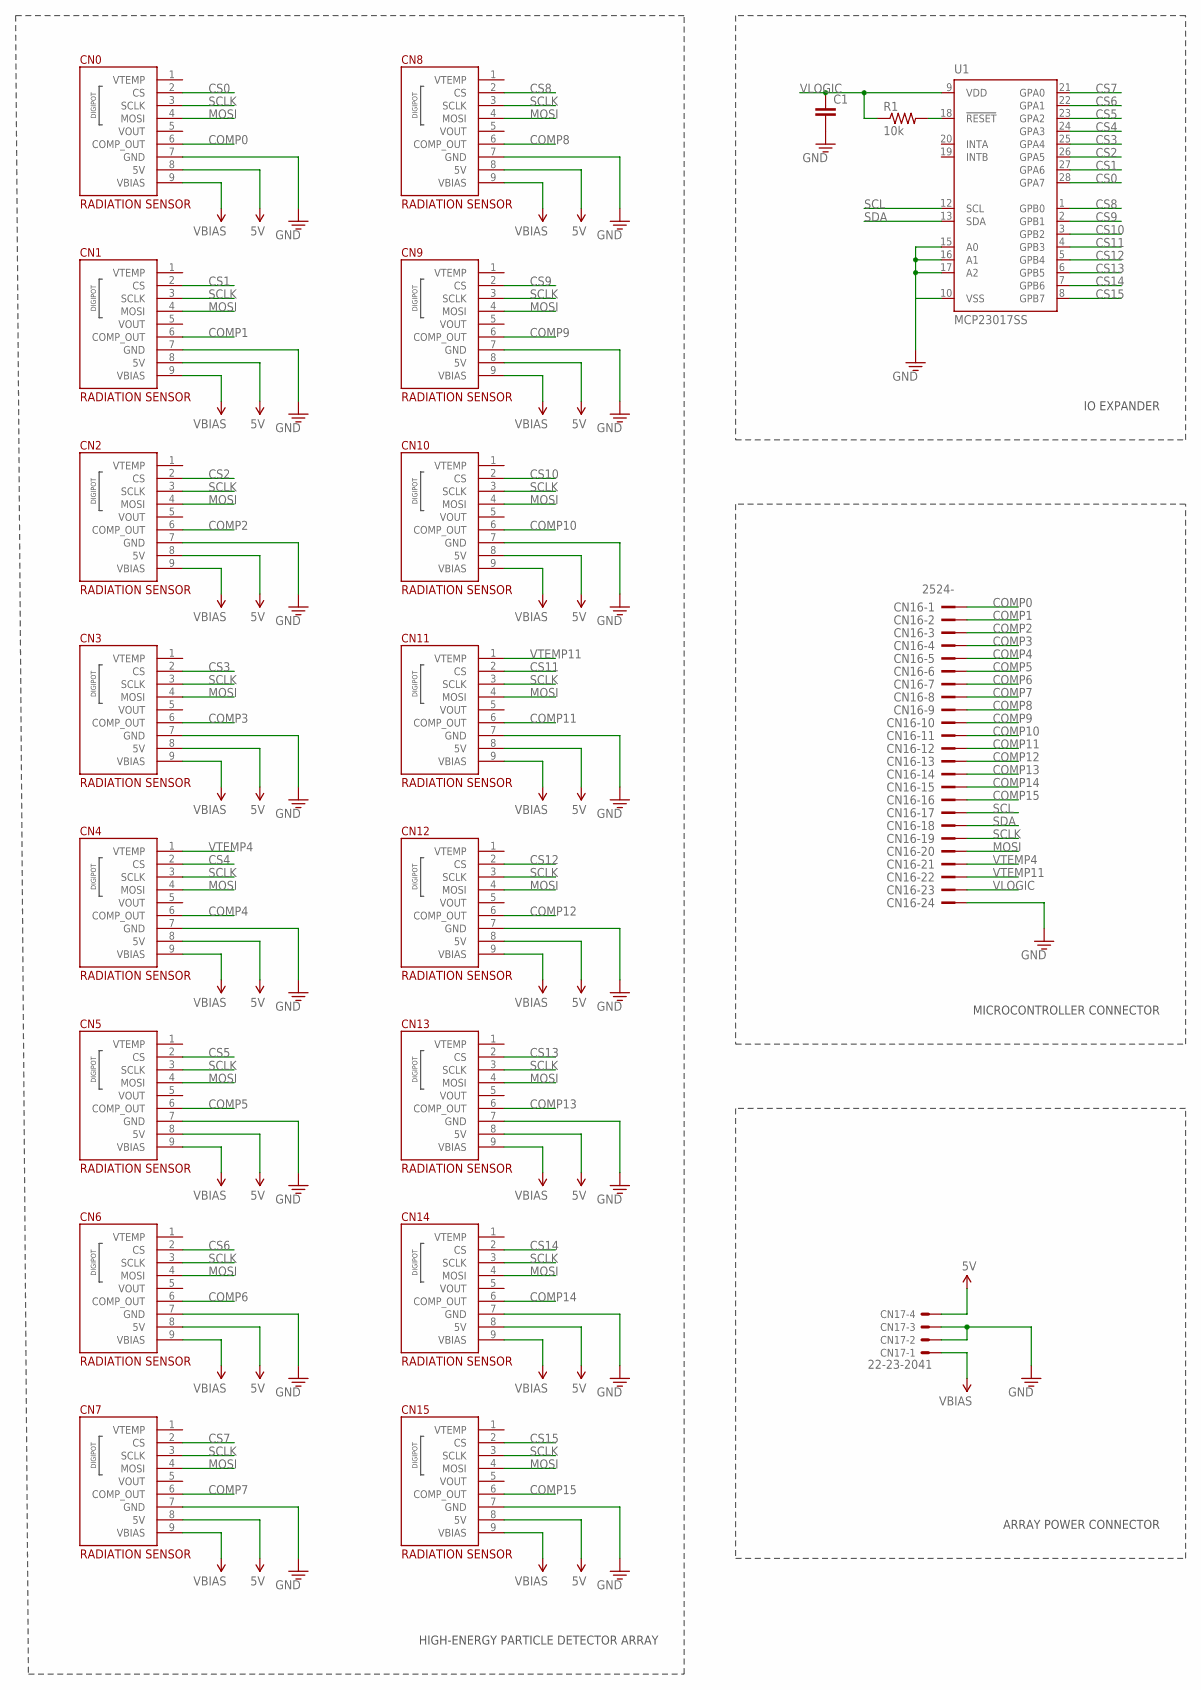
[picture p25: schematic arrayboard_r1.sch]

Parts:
C1: CAP0603; 0603
CN0, CN1, CN2, CN3, CN4, CN5, CN6, CN7, CN8, CN9, CN10, CN11, CN12, CN13, CN14, CN15: RADIATION-SENSOR-REV1
CN16: 2524-; PAK100/2500-24
CN17: 22-23-2041
R1: 10k; 0603
U1: MCP23017SS; SSOP28

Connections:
5V: CN0.8 (5V), CN1.8 (5V), CN2.8 (5V), CN3.8 (5V), CN4.8 (5V), CN5.8 (5V), CN6.8 (5V), CN7.8 (5V), CN8.8 (5V), CN9.8 (5V), CN10.8 (5V), CN11.8 (5V), CN12.8 (5V), CN13.8 (5V), CN14.8 (5V), CN15.8 (5V), CN17.4
COMP0: CN0.6 (COMP_OUT), CN16.1
COMP1: CN1.6 (COMP_OUT), CN16.2
COMP2: CN2.6 (COMP_OUT), CN16.3
COMP3: CN3.6 (COMP_OUT), CN16.4
COMP4: CN4.6 (COMP_OUT), CN16.5
COMP5: CN5.6 (COMP_OUT), CN16.6
COMP6: CN6.6 (COMP_OUT), CN16.7
COMP7: CN7.6 (COMP_OUT), CN16.8
COMP8: CN8.6 (COMP_OUT), CN16.9
COMP9: CN9.6 (COMP_OUT), CN16.10
COMP10: CN10.6 (COMP_OUT), CN16.11
COMP11: CN11.6 (COMP_OUT), CN16.12
COMP12: CN12.6 (COMP_OUT), CN16.13
COMP13: CN13.6 (COMP_OUT), CN16.14
COMP14: CN14.6 (COMP_OUT), CN16.15
COMP15: CN15.6 (COMP_OUT), CN16.16
CS0: CN0.2 (CS), U1.28 (GPA7)
CS1: CN1.2 (CS), U1.27 (GPA6)
CS2: CN2.2 (CS), U1.26 (GPA5)
CS3: CN3.2 (CS), U1.25 (GPA4)
CS4: CN4.2 (CS), U1.24 (GPA3)
CS5: CN5.2 (CS), U1.23 (GPA2)
CS6: CN6.2 (CS), U1.22 (GPA1)
CS7: CN7.2 (CS), U1.21 (GPA0)
CS8: CN8.2 (CS), U1.1 (GPB0)
CS9: CN9.2 (CS), U1.2 (GPB1)
CS10: CN10.2 (CS), U1.3 (GPB2)
CS11: CN11.2 (CS), U1.4 (GPB3)
CS12: CN12.2 (CS), U1.5 (GPB4)
CS13: CN13.2 (CS), U1.6 (GPB5)
CS14: CN14.2 (CS), U1.7 (GPB6)
CS15: CN15.2 (CS), U1.8 (GPB7)
GND: C1.2, CN0.7 (GND), CN1.7 (GND), CN2.7 (GND), CN3.7 (GND), CN4.7 (GND), CN5.7 (GND), CN6.7 (GND), CN7.7 (GND), CN8.7 (GND), CN9.7 (GND), CN10.7 (GND), CN11.7 (GND), CN12.7 (GND), CN13.7 (GND), CN14.7 (GND), CN15.7 (GND), CN16.24, CN17.2, CN17.3, U1.10 (VSS), U1.15 (A0), U1.16 (A1), U1.17 (A2)
MOSI: CN0.4 (MOSI), CN1.4 (MOSI), CN2.4 (MOSI), CN3.4 (MOSI), CN4.4 (MOSI), CN5.4 (MOSI), CN6.4 (MOSI), CN7.4 (MOSI), CN8.4 (MOSI), CN9.4 (MOSI), CN10.4 (MOSI), CN11.4 (MOSI), CN12.4 (MOSI), CN13.4 (MOSI), CN14.4 (MOSI), CN15.4 (MOSI), CN16.20
unnamed: R1.2, U1.18 (!RESET)
SCL: CN16.17, U1.12 (SCL)
SCLK: CN0.3 (SCLK), CN1.3 (SCLK), CN2.3 (SCLK), CN3.3 (SCLK), CN4.3 (SCLK), CN5.3 (SCLK), CN6.3 (SCLK), CN7.3 (SCLK), CN8.3 (SCLK), CN9.3 (SCLK), CN10.3 (SCLK), CN11.3 (SCLK), CN12.3 (SCLK), CN13.3 (SCLK), CN14.3 (SCLK), CN15.3 (SCLK), CN16.19
SDA: CN16.18, U1.13 (SDA)
VBIAS: CN0.9 (VBIAS), CN1.9 (VBIAS), CN2.9 (VBIAS), CN3.9 (VBIAS), CN4.9 (VBIAS), CN5.9 (VBIAS), CN6.9 (VBIAS), CN7.9 (VBIAS), CN8.9 (VBIAS), CN9.9 (VBIAS), CN10.9 (VBIAS), CN11.9 (VBIAS), CN12.9 (VBIAS), CN13.9 (VBIAS), CN14.9 (VBIAS), CN15.9 (VBIAS), CN17.1
VLOGIC: C1.1, CN16.23, R1.1, U1.9 (VDD)
VTEMP4: CN4.1 (VTEMP), CN16.21
VTEMP11: CN11.1 (VTEMP), CN16.22

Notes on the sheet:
HIGH-ENERGY PARTICLE DETECTOR ARRAY
ARRAY POWER CONNECTOR
MICROCONTROLLER CONNECTOR
IO EXPANDER

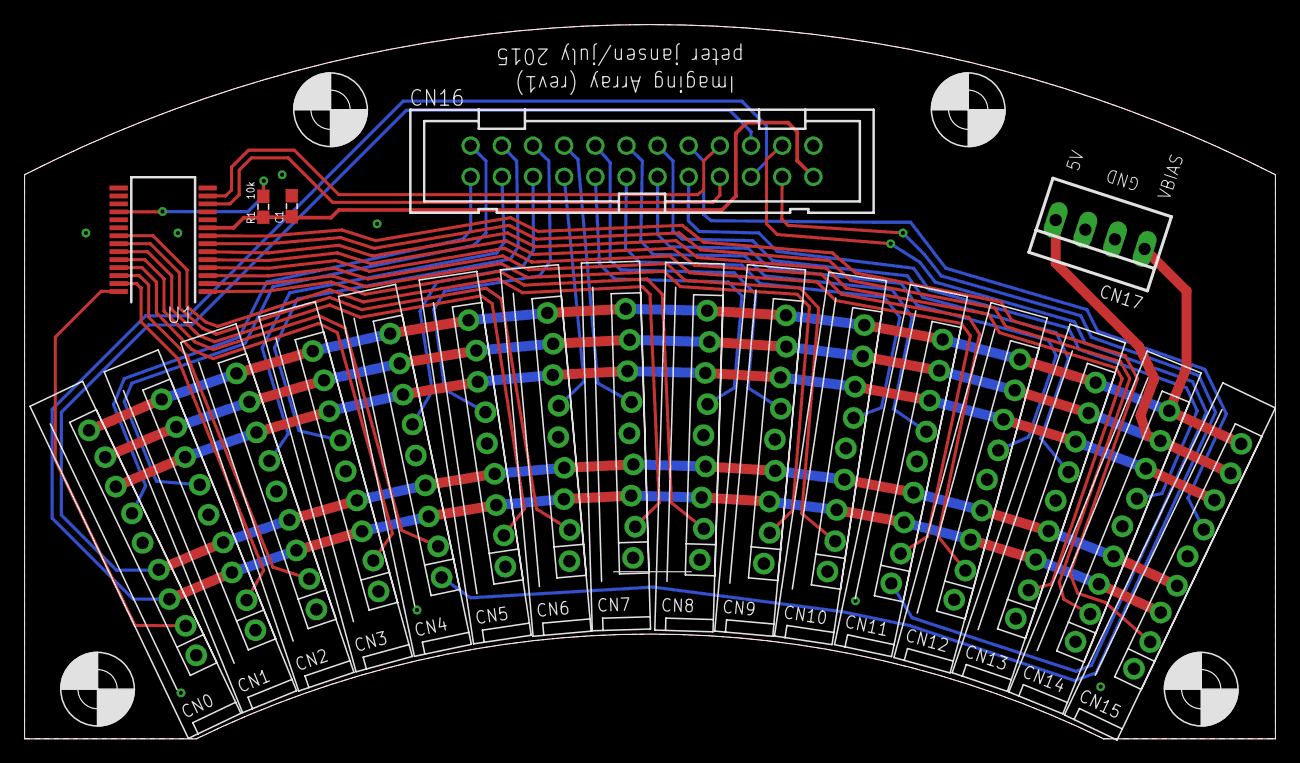
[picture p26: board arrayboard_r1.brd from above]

Board: 2 copper layers, 102.0 x 58.2 mm, 25 parts (0 on the bottom side), 43 nets.

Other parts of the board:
U$35, U$36, U$37, U$38: MOUNT-M3

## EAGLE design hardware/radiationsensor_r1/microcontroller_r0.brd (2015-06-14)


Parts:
CN1: 2524-; PAK100/2500-24
JP1: M04LOCK; 1X04_LOCK
R1, R2: 10k; 0603
U1: ARDUINO_PRO_MINI

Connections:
5V: CN1.24, JP1.4, R1.2, R2.1, U1.21 (VCC)
COMP0: CN1.2, U1.5 (2)
COMP1: CN1.1, U1.6 (*3)
COMP2: CN1.4, U1.7 (4)
COMP3: CN1.3, U1.8 (*5)
COMP4: CN1.6, U1.9 (*6)
COMP5: CN1.5, U1.10 (7)
COMP6: CN1.8, U1.11 (8)
COMP7: CN1.7, U1.12 (*9)
COMP8: CN1.10, U1.19 (A2)
COMP9: CN1.9, U1.20 (A3)
COMP10: CN1.12, U1.17 (A0)
COMP11: CN1.11, U1.18 (A1)
COMP12: CN1.14, U1.A6
COMP13: CN1.13, U1.A7
COMP14: CN1.16, U1.13 (*10)
COMP15: CN1.15, U1.14 (*11)
GND: CN1.23, JP1.1, U1.4 (GND), U1.23 (GND)
MOSI: CN1.19, U1.15 (12)
SCL: CN1.18, R2.2, U1.A5
SCLK: CN1.20, U1.16 (13)
SDA: CN1.17, R1.1, U1.A4
VTEMP4: CN1.22, JP1.2
VTEMP11: CN1.21, JP1.3

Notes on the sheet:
MICROCONTROLLER CONNECTOR



Board: 2 copper layers, 36.0 x 43.2 mm, 7 parts (4 on the bottom side), 24 nets.

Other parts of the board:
U$35, U$36: MOUNT-M3

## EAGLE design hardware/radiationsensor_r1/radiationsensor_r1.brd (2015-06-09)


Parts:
C1: 0.01uF 50V; 0603
C2: 4.7pF; 0603
C3, C10, C11, C12, C13: 0.1uF; 0603
C4: 1uF 50V; 0603
C5: 1000pF; 0603
C6: 4.7uF; 0603
C7, C9: 100pF; 0603
C8: 0.01uF; 0603
C14: 10uF 10V; 0805
C15: 0.1uF 50V; 0603
C16: 1uF; 0603
CN1: 1X09
CN2: GROUND-PAD
D1: BPW34S; BPW34S-4STACK-SIDEMOUNT
R1, R13: 1M; 0603
R2: 10M; 0603
R3: 47M; 0603
R4, R6: 1k; 0603
R5, R7: 33k; 0603
R8, R9, R10, R11: 51k; 0603
R12: 3.3k; 0603
R14: 190k; 0603
R15: 165k; 0603
R16: NCP18XV103; 0603
R17: 10k; 0603
U1: LMP7721; SOIC-8
U2, U4: MAX4477; SOIC-8
U5: 50k; SOT-23-8

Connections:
5V: C3.1, C6.1, C12.1, C14.1, C16.1, CN1.8, R8.2, R10.2, R15.2, R17.2, U1.6 (VCC), U2.8 (V+), U4.8 (V+), U5.2 (VDD)
COMP_OUT: CN1.6, R13.2, U4.7 (OUT)
CS: CN1.2, U5.6 (CS#)
GND: C3.2, C4.2, C6.2, C10.2, C12.2, C13.2, C14.2, C15.2, C16.2, CN1.7, CN2.GND, D1.A (ANODE), R9.1, R11.1, R14.1, R16.1, U1.3 (GND), U2.4 (V-), U4.4 (V-), U5.3 (GND)
MOSI: CN1.4, U5.5 (SDI)
unnamed: C1.2, C2.1, R3.1, U1.8 (-)
unnamed: C1.1, D1.C (CATHODE), R2.1
unnamed: C7.2, C8.1, R5.2, U2.1 (OUT)
unnamed: C4.1, R1.1, R2.2
unnamed: C7.1, R4.2, R5.1, U2.2 (-)
unnamed: C5.2, R4.1
unnamed: C2.2, C5.1, R3.2, U1.4 (OUT)
unnamed: C9.1, R6.2, R7.1, U2.6 (-)
unnamed: C8.2, R6.1
unnamed: C11.2, R10.1, R11.2, U4.3 (+)
unnamed: C9.2, C11.1, R7.2, U2.7 (OUT)
unnamed: R12.2, R13.1, U4.5 (+)
unnamed: R15.1, U5.8 (A)
SCLK: CN1.3, U5.4 (CLK)
V/2: C10.1, R8.1, R9.2, U1.1 (+), U1.2 (G1), U1.7 (G2), U2.3 (+), U2.5 (+)
VBIAS: C15.1, CN1.9, R1.2
VOUT: CN1.5, R12.1, U4.1 (OUT), U4.2 (-)
VTEMP: CN1.1, R16.2, R17.1
V_COMP: C13.1, R14.2, U4.6 (-), U5.1 (W)

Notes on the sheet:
PREAMPLIFIER
AMPLIFIER
AC COUPLER
COMPARATOR
VOLTAGE REFERENCE
(V/2)
(COMPARATOR, ADJUSTABLE)
USER INTERFACE
(~15mv HYSTERESIS)
(~1100X GAIN)
DECOUPLING
TEMPERATURE SENSOR
PETER JANSEN, JUNE 2015
RADIATION SENSOR (REVISION 1)
BASED ON MAXIM APPLICATION NOTE 2236
(STACK OF 4
PHOTODIODES)


Board: 2 copper layers, 30.0 x 48.5 mm, 40 parts (1 on the bottom side), 24 nets.

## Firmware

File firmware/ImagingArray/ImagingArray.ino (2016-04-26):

// OpenCT2 Imaging Array Controller/Parser
// Peter Jansen, October/2015
// 
// Usage: Accepts serial commands of the form <char> <int_argument> <optional int_argument>, 
// Where: A <1-255> sets the digipot threshold for all channels
// D <1-16> <1-255> sets the digipot threshold for a particular channel (1-16)
// I <1-600> measures/integrates from all channels for 1-600 seconds, and displays the results
//
// Requires: Adafruit MCP23017 and MCP23008 I/O Expander Libraries

#include <Wire.h>
#include "Adafruit_MCP23017.h"
#include "Adafruit_MCP23008.h"

// Global objects
Adafruit_MCP23017 IOExpander;       // I/O expander for detector CS lines (on imaging array board)
Adafruit_MCP23008 IOExpanderSPI;    // I/O expander for SPI lines (on microcontroller board)

// Sensor channels
#define MAX_CHANNELS   16
#define MAX_HISTBINS   10

// Sensor data
uint16_t channelCounts[MAX_CHANNELS]; 
long unsigned int channelLastTimes[MAX_CHANNELS];
long unsigned int channelStartTimes[MAX_CHANNELS];
uint16_t channelHist[MAX_CHANNELS][MAX_HISTBINS]; 

#define MAX_COUNTS_PER_CHANNEL  64000
 
// Radiation sensor detections are active high 
#define SENSOR_ACTIVE   1
#define SENSOR_INACTIVE 0

// Channel debounce time (in microseconds).  No counts will be made if the last count was within this time. 
#define SENSOR_DEBOUNCETIME  150

// Pin Definitions (SPI/Digipot).  These are pin numbers on the MCP23008 I/O expander
#define DIGIPOT_MOSI  0 
#define DIGIPOT_SCLK  1

// Pin Definitions (Sensor Channels)
#define CH0    A2
#define CH1    A3
#define CH2    A0
#define CH3    A1
#define CH4    12
#define CH5    13
#define CH6    10
#define CH7    11
#define CH8    3
#define CH9    2
#define CH10   5
#define CH11   4
#define CH12   7
#define CH13   6
#define CH14   9 
#define CH15   8

// Port/Pin definitions for interrupt map
// PB0(8), PB1(9), PB2(10), PB3(11), PB4(12), PB5(13) 
#define chPB0  15
#define chPB1  14
#define chPB2  6
#define chPB3  7
#define chPB4  4
#define chPB5  5


// PC0(AD0), PC1(AD1), PC2(AD2), PC3(AD3), PC4(AD4/SDA), PC5(AD5/SCL)
#define chPC0  2
#define chPC1  3
#define chPC2  0
#define chPC3  1
// Note, missing channels 12/13 (AD6/AD7)

// PD0(0/RXI), PD1(0/TXD), PD2(2), PD3(3), PD4(4), PD5(5), PD6(6), PD7(7)
#define chPD2  9  
#define chPD3  8
#define chPD4  11
#define chPD5  10
#define chPD6  13
#define chPD7  12


// Serial/Error messages
#define SERIAL_WELCOME_MESSAGE        "OpenCT2 Imaging Array Controller"
#define SERIAL_WELCOME_MESSAGE2       "Commands: " 
#define SERIAL_WELCOME_MESSAGE3       "Set all digipots: A <1-255>"
#define SERIAL_WELCOME_MESSAGE4       "Set digipot on one channel: D <1-16> <1-255>"
#define SERIAL_WELCOME_MESSAGE5       "Integrate/measure: I <seconds>"
#define SERIAL_PARSE_ERROR            "UNRECOGNIZED INPUT"
#define SERIAL_SUCCESSFUL_COMMAND     "OK"
#define SERIAL_PROMPT                 "> "



/*
 * MCP23017 I/O Expander
 */ 
 
#define CS_INACTIVE  1
#define CS_ACTIVE    0
 
// Initialize the I/O expander
void setupIOExpander() {
  // MCP23017 I/O Expander  (for detector CS lines)
  IOExpander.begin();                        // Use default address (0)

  // Set all pins (which are chip selects) to outputs  
  for (int i=0; i<16; i++) {
    IOExpander.pinMode(i, OUTPUT);
  }  
  
  // Set all values to inactive
  for (int i=0; i<16; i++) {
    setCS(i, CS_INACTIVE);
  }  
  
}

// Set the chip select value on a given channel
void setCS(uint8_t channel, uint8_t value) {
  uint8_t channelMap[16];
  channelMap[0] = 7;
  channelMap[1] = 6;
  channelMap[2] = 5;
  channelMap[3] = 4;
  channelMap[4] = 3;
  channelMap[5] = 2;
  channelMap[6] = 1;
  channelMap[7] = 0;

  //## Note, below may be in reversed order
  /*
  channelMap[8] = 15;
  channelMap[9] = 14;
  channelMap[10] = 13;
  channelMap[11] = 12;
  channelMap[12] = 11;
  channelMap[13] = 10;
  channelMap[14] = 9;
  channelMap[15] = 8;
*/
  channelMap[8] = 8;
  channelMap[9] = 9;
  channelMap[10] = 10;
  channelMap[11] = 11;
  channelMap[12] = 12;
  channelMap[13] = 13;
  channelMap[14] = 14;
  channelMap[15] = 15;

  
  IOExpander.digitalWrite(channelMap[channel], value);
  
}

/*
 * Digipot
 */ 
void setupDigipot() {
  // MCP23008 I/O Expander (for SPI lines)
  IOExpanderSPI.begin(7);     // Address lines are all high (7)

  // Set all pins to inputs as default (most are unused)
  for (int i=0; i<16; i++) {
    IOExpanderSPI.pinMode(i, INPUT);
  }  

  // Set SPI lines to output
  IOExpanderSPI.pinMode(DIGIPOT_MOSI, OUTPUT);
  IOExpanderSPI.pinMode(DIGIPOT_SCLK, OUTPUT);   
}
 

void setDigipot(uint8_t channel, uint8_t value) {
  // Idle
  uint8_t val = value;
  IOExpanderSPI.digitalWrite(DIGIPOT_SCLK, 1);
  delay(2);
  setCS(channel, CS_ACTIVE);
  delay(2);  
  
  for (int i=0; i<8; i++) {
    IOExpanderSPI.digitalWrite(DIGIPOT_SCLK, 0);        // Inactive
    delay(1);
    
    // Data
    if ((val & 0x80) > 0) {
      IOExpanderSPI.digitalWrite(DIGIPOT_MOSI, 1);
      // Serial.print("1");
    } else {
      IOExpanderSPI.digitalWrite(DIGIPOT_MOSI, 0);
      // Serial.print("0");      
    }
    val = val << 1;
    delay(1);
    
    IOExpanderSPI.digitalWrite(DIGIPOT_SCLK, 1);      // Active
    delay(2);
      
  }
  
  IOExpanderSPI.digitalWrite(DIGIPOT_SCLK, 0);      // Active
  delay(2);
  
  setCS(channel, CS_INACTIVE);  
  // Serial.println("");
}
 
// Set all Digipot channels to a given value 
void setAllDigipotChannels(uint8_t value) {
  for (int i=0; i<MAX_CHANNELS; i++) {
    setDigipot(i, value); 
  }  
}
 
/*
 * Detector Channel Interrupt Initialization
 */
 
// Set the pins for all sensor channels to input
void setupSensorChannelPins() {
  pinMode(CH0, INPUT); 
  pinMode(CH1, INPUT);
  pinMode(CH2, INPUT);
  pinMode(CH3, INPUT);
  pinMode(CH4, INPUT);
  pinMode(CH5, INPUT);
  pinMode(CH6, INPUT);
  pinMode(CH7, INPUT);
  pinMode(CH8, INPUT);
  pinMode(CH9, INPUT);
  pinMode(CH10, INPUT);
  pinMode(CH11, INPUT);
  pinMode(CH12, INPUT);
  pinMode(CH13, INPUT);
  pinMode(CH14, INPUT);  
  pinMode(CH15, INPUT);    
}

// Enable pin change interrupt on all channels 
void enableSensorChannelInterrupts() {
  enablePCI(CH0);
  enablePCI(CH1);
  enablePCI(CH2);
  enablePCI(CH3);
  enablePCI(CH4);
  enablePCI(CH5);
  enablePCI(CH6);        
  enablePCI(CH7);
  enablePCI(CH8);
  enablePCI(CH9);
  enablePCI(CH10);
  enablePCI(CH11);
  enablePCI(CH12);
  enablePCI(CH13);
  enablePCI(CH14);  
  enablePCI(CH15);    
}

 
/*
 * Pin change interrupts
 */ 
void enablePCI(byte pin) {
  *digitalPinToPCMSK(pin) |= bit (digitalPinToPCMSKbit(pin));    // enable pin
  PCIFR  |= bit (digitalPinToPCICRbit(pin));                     // clear any outstanding interrupt
  PCICR  |= bit (digitalPinToPCICRbit(pin));                     // enable interrupt for the group
}
 
#define maskB0  B00000001
#define maskB1  B00000010
#define maskB2  B00000100
#define maskB3  B00001000
#define maskB4  B00010000
#define maskB5  B00100000
#define maskB6  B01000000
#define maskB7  B10000000

// ISR for PORT B (pins D8-D13)
uint8_t lastPORTB = 0;
ISR (PCINT0_vect) {
  uint8_t curPORTB = PINB;                                      // get pin states
  uint8_t diff = lastPORTB ^ curPORTB;                          // find differences between current and last states  
  
  if ((diff & maskB0) > 0)    countPin(chPB0, bitRead(curPORTB, 0));  
  if ((diff & maskB1) > 0)    countPin(chPB1, bitRead(curPORTB, 1));
  if ((diff & maskB2) > 0)    countPin(chPB2, bitRead(curPORTB, 2));
  if ((diff & maskB3) > 0)    countPin(chPB3, bitRead(curPORTB, 3));  
  if ((diff & maskB4) > 0)    countPin(chPB4, bitRead(curPORTB, 4));  
  if ((diff & maskB5) > 0)    countPin(chPB5, bitRead(curPORTB, 5));  

  lastPORTB = curPORTB;  
}

 
// ISR for PORT C (pins A0-A5)
uint8_t lastPORTC = 0;
ISR (PCINT1_vect) {
  uint8_t curPORTC = PINC;                                      // get pin states
  uint8_t diff = lastPORTC ^ curPORTC;                          // find differences between current and last states  
  lastPORTC = curPORTC;  
    
  if ((diff & maskB0) > 0)    countPin(chPC0, curPORTC & maskB0);
  if ((diff & maskB1) > 0)    countPin(chPC1, curPORTC & maskB1);
  if ((diff & maskB2) > 0)    countPin(chPC2, curPORTC & maskB2);
  if ((diff & maskB3) > 0)    countPin(chPC3, curPORTC & maskB3);
  
  
}  

// ISR for PORT D (pins D0-D7)
uint8_t lastPORTD = 0;
ISR (PCINT2_vect) {
  uint8_t curPORTD = PIND;                                      // get pin states
  uint8_t diff = lastPORTD ^ curPORTD;                          // find differences between current and last states  
  lastPORTD = curPORTD;
  
  if ((diff & maskB2) > 0)    countPin(chPD2, curPORTD & maskB2);
  if ((diff & maskB3) > 0)    countPin(chPD3, curPORTD & maskB3);
  if ((diff & maskB4) > 0)    countPin(chPD4, curPORTD & maskB4);
  if ((diff & maskB5) > 0)    countPin(chPD5, curPORTD & maskB5);
  if ((diff & maskB6) > 0)    countPin(chPD6, curPORTD & maskB6);
  if ((diff & maskB7) > 0)    countPin(chPD7, curPORTD & maskB7);  
}  
  
/*
 * Counting
 */ 

// Set all counts to zero 
void clearCounts() {
  for (int i=0; i<MAX_CHANNELS; i++) {
    channelCounts[i] = 0;
    channelLastTimes[i] = 0;
    channelStartTimes[i] = 0;
    
    for (int j=0; j<MAX_HISTBINS; j++) {
      channelHist[i][j] = 0;
    }
  }
}
  
// This is the main function that performs counting.  It should be called twice -- once when the pin initially becomes 
// active, and again when the pin becomes inactive.  It calculates both number of counts, and a histogram of pulse-width times. 
inline void countPin(uint8_t channel, uint8_t state) {
/*  
  Serial.print("CH");
  Serial.print(channel);  
  Serial.print(" ");
  Serial.print(state, BIN);
  Serial.println("");
*/  
  
  if (state > 0) {
      // Transitioning to active state
      channelStartTimes[channel] = micros();                       // Store start time of pulse (for determining pulse length)
  } else {
    // Transitioning to inactive state
      long unsigned int curTime = micros();
      long unsigned int deltaTime = curTime - channelLastTimes[channel];
      long unsigned int pulseWidthTime = curTime - channelStartTimes[channel];
      if (deltaTime > SENSOR_DEBOUNCETIME) {                      // Debounce
        if (channelCounts[channel] < MAX_COUNTS_PER_CHANNEL) {      // Prevent overflow errors
          channelCounts[channel] += 1;                              // Increment channel count
          uint8_t histBin = (pulseWidthTime >> 2)-3;                // Calculate histogram bin (NOTE: millis() has a resolution of 4uSec, and is always a multiple of four)
          if (histBin >= MAX_HISTBINS) histBin = MAX_HISTBINS-1;    // Last histogram bin is a catch-all
          channelHist[channel][histBin] += 1;                       // Increment histogram bin count
          channelLastTimes[channel] = micros();                     // Store start time of pulse (for debouncing)       
        }
      }
  }
} 
 
 
 
/*
 * Display
 */
void displayChannel(uint8_t channel) {
  Serial.print(channel);
  Serial.print("\t");
  Serial.print(channelCounts[channel]);
  Serial.println("");
} 
 
void displayChannelHist(uint8_t channel) {
  Serial.print(channel);
  Serial.print("\t");
  Serial.print(channelCounts[channel]);
  Serial.print("\t");
  
  for (int bin=0; bin<MAX_HISTBINS; bin++) {
    Serial.print(channelHist[channel][bin]);
    Serial.print("\t");
  }
  Serial.println("");
} 

void displayAllChannels() {
  for (int i=0; i<MAX_CHANNELS; i++) {
    displayChannel(i);
  } 
}

void displayAllChannelsHist() {
  for (int i=0; i<MAX_CHANNELS; i++) {
    displayChannelHist(i);
  } 
}

void displayCountsCondensed() {
  for (int i=0; i<MAX_CHANNELS; i++) {
    Serial.print(channelCounts[i]);
    Serial.print("\t");
  }   
  Serial.println("");
}
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

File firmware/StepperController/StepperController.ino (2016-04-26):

// OpenCT2 Stepper Controller/Parser
// Peter Jansen, October/2015
// 
// Usage: Accepts serial commands of the form <char> <int_argument>, 
// Where: <char> defines the axis of motion (either R or Z)
// <int_argument> defines how many steps to move, between -255 and 255. 
//
// Requires: Adafruit Motor Shield Library

#include <Wire.h>
#include <Adafruit_MotorShield.h>
#include <Adafruit_PWMServoDriver.h>

// Pin Definitions
#define SWITCH_ZHOMELIMIT   12
#define SWITCH_ZTOPLIMIT    13
#define RELAY_VBIAS         10

// Constants
#define Z_AXIS  1
#define R_AXIS  2

// Step modes in the stepper driver.  Valid modes are: SINGLE, DOUBLE, INTERLEAVE, MICROSTEP
#define Z_STEP_MODE   DOUBLE
#define R_STEP_MODE   INTERLEAVE

// Scaling factor for Z axis
#define ZSCALE  10

// Error messages
#define SERIAL_WELCOME_MESSAGE        "OpenCT2 Motion Controller"
#define SERIAL_WELCOME_MESSAGE2       "Format: <char> <int>, where <char> = R,Z and <int> = -255 to 255"
#define SERIAL_WELCOME_MESSAGE3       "Other commands: H 1 (Home Z axis), L 1 (display limit switch state)"
#define SERIAL_PARSE_ERROR            "UNRECOGNIZED INPUT"
#define SERIAL_SUCCESSFUL_COMMAND     "OK"
#define SERIAL_PROMPT                 "> "


// Motor Shield
// Create the motor shield object with the default I2C address
Adafruit_MotorShield AFMS = Adafruit_MotorShield(); 

// Connect a stepper motor with 200 steps per revolution (1.8 degree)
// to motor port #2 (M3 and M4)
Adafruit_StepperMotor *zAxisMotor = AFMS.getStepper(200, 2);
Adafruit_StepperMotor *rAxisMotor = AFMS.getStepper(200, 1);



// Moves the Z or R axes
void moveAxes(int whichAxis, int distance) {
  
  switch(whichAxis) {
    case Z_AXIS:
      // The Z axis has a fine pitched lead screw, so multiply the distance by zScale so that we don't have to 
      // send large numbers over the serial console    
      if (distance > 0) {
        for (int i=0; i<distance; i++) {
          if (limitTop() == false) {
            zAxisMotor->step(1 * ZSCALE, FORWARD, Z_STEP_MODE);
          }
        }
      } else {
        for (int i=0; i<-distance; i++) {
          if (limitHome() == false) {
            zAxisMotor->step(1 * ZSCALE, BACKWARD, Z_STEP_MODE);   
          }
        }    
      }
      
      // Turn off Z stepper 
      zAxisMotor->release();
      break;
      
    case R_AXIS:
      // Rotational Axis
      if (distance > 0) {
        rAxisMotor->step(distance, FORWARD, R_STEP_MODE); 
      } else {
        rAxisMotor->step(-distance, BACKWARD, R_STEP_MODE);       
      }

      // Turn off Z stepper 
      rAxisMotor->release();      
      break;
      
    default:
      // Error: Axis not recognized
      break;
  }
    
}
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

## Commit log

2015-03-18 Added beginnings of radiation detector schematic
    [notes1a.brd, notes1a.sch]
2015-03-19 Added PIC microcontroller
    [notes1a.brd, notes1a.sch]
2015-03-19 Added photodiode preamplifier
    [notes1a.brd, notes1a.sch]
2015-04-29 Added first revision of radiation sensor design
    [notes1a.brd, notes1a.sch, radiationsensor_r0.GBL, radiationsensor_r0.GBO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]
2015-06-05 Starting radiation sensor rev1
    [radiationsensor_r1.brd, radiationsensor_r1.sch]
2015-06-05 minor changes
    [radiationsensor_r1.brd]
2015-06-06 radiation sensor r1 layout nearly complete
    [radiationsensor_r1.brd, radiationsensor_r1.sch]
2015-06-07 schematic and board cleanup
    [radiationsensor_r1.brd, radiationsensor_r1.sch]
2015-06-07 Added part in library for radiation sensor rev1
    [radiationsensor_r1.brd, radiationsensor_r1.sch]
2015-06-07 Added beginnings of 2.25inch dia parallel array board
    [arrayboard_r0.brd, arrayboard_r0.sch, radiationsensor_r1.brd]
2015-06-07 Progress on array board/schematic
    [arrayboard_r0a.brd, arrayboard_r0a.sch]
2015-06-07 Added breakout pattern to array
    [arrayboard_r0a.brd]
2015-06-07 breakout pattern cleanup
    [arrayboard_r0a.brd]
2015-06-07 basic layout (not including microcontroller)
    [arrayboard_r0a.brd, arrayboard_r0a.sch]
2015-06-08 Added connector an IO expander
    [arrayboard_r0a.brd, arrayboard_r0a.sch]
2015-06-08 connector and IO expander nearly wired
    [arrayboard_r0a.brd, arrayboard_r0a.sch]
2015-06-08 basic layout complete
    [arrayboard_r0a.brd, arrayboard_r0a.sch]
2015-06-08 started board outline and ground plane
    [arrayboard_r0a.brd]
2015-06-09 Board outline and ground planes complete
    [arrayboard_r0a.brd]
2015-06-09 mechanical bits
    [arrayboard_r0a.brd, arrayboard_r0a.sch]
2015-06-09 final cleanup
    [arrayboard_r0.brd, arrayboard_r0.sch, arrayboard_r0a.brd]
2015-06-09 minor cleanup
    [arrayboard_r0a.brd, arrayboard_r0a.sch]
2015-06-09 Added shield connection to radiation sensor rev1
    [radiationsensor_r1.brd, radiationsensor_r1.sch]
2015-06-09 Minor clearance change to array board
    [arrayboard_r0.brd]
2015-06-10 schematic cleanup
    [arrayboard_r0.sch]
2015-06-14 Added microcontroller board rev0
    [microcontroller_r0.brd, microcontroller_r0.sch]
2015-06-18 added PDFs of schematics
    [arrayboard_r0.sch]
2015-06-27 Added partslist for Radiation Sensor r1
2015-07-09 Added rough mechanical layout for imaging array board rev1
    [arrayboard_r1.brd, arrayboard_r1.sch]
2015-07-10 partial routing for imaging array rev1
    [arrayboard_r1.brd]
2015-07-10 additional routing
    [arrayboard_r1.brd]
2015-07-11 finished routing for imaging array board rev1
    [arrayboard_r1.brd, arrayboard_r1.sch]
2015-07-11 Added imaging array rev1 gerbers and pdf schematic
    [arrayboard_r1.brd]
2015-08-05 Added microcontroller rev1 board
    [microcontroller_r1.brd, microcontroller_r1.sch]
2015-09-07 Initial commits of detector platform and table bearing holder
2015-09-07 Initial source mount design and modifications to detector platform to mount it
2015-10-10 Added stepper controller firmware
2015-12-12 Mounts for electronics (pi, arduino, relay, usb hub) in bottom of unit
2016-01-01 Beginning main power supply board
    [powersupply_r0.brd, powersupply_r0.sch]
2016-01-01 more basic placement and shape
    [powersupply_r0.brd, powersupply_r0.sch]
2016-01-01 basic placement
    [powersupply_r0.brd, powersupply_r0.sch]
2016-01-02 component layout complete
    [powersupply_r0.brd, powersupply_r0.sch]
2016-01-02 major routing on power supply board
    [powersupply_r0.brd, powersupply_r0.sch]
2016-01-02 ground plane routing
    [powersupply_r0.brd]
2016-01-02 cleanup and silkscreen
    [powersupply_r0.brd, powersupply_r0.sch]
2016-01-02 Added power supply rev0 gerbers and images
    [powersupply_r0.brd]
2016-01-02 Added power supply partslist
2016-01-07 Added limit switch sketchup and STL file for Z axis
    [limitswitch_mount1a.skp, limitswitch_mount1a_fixed.stl]
2016-01-08 minor changes to powersuppy partslist
2016-01-11 Added initial port of the SSD1351 display driver to the Raspberry Pi 2 with the wiringPi library
2016-01-12 Added OLED navigation screen for raspberry pi
    [navscreen_r0.brd, navscreen_r0.sch]
2016-01-12 Added navigation screen interface board for the raspberry pi 2
    [navscreen_piboard_r0.brd, navscreen_piboard_r0.sch]
2016-01-14 Added gerbers and images for navigation screen boards
2016-02-14 Added first prototype of keyed table
2016-02-14 Added mount point for navigation screen prototype
2016-03-13 Added nutholder and shield mount sketchup files
    [notes_nutholder2a2.skp, shield_mount1a.skp]
2016-03-13 Added shield mount STL file
    [shield_mount1a_fixed.stl]
2016-03-14 Added mount holes for cabling to structural plates
2016-03-15 minor mechanical change to shield mount
    [shield_mount1a.skp, shield_mount1a_fixed.stl]
2016-03-20 Added Z limit switches to StepperController
2016-03-27 Minor changes -- added limit switch monitor to StepperController, and Python serial test
2016-03-28 Beginnings of calibration program
2016-03-28 Added text files showing led bug
2016-03-30 Minor changes -- calibration test now outputs to file. Long runs seem to freeze -- likely an issue with the waitForResponse() serial function, and timing
2016-03-31 Added timeout/error detection and automatic retries to serial code for python detector calibration script
2016-03-31 Added initial calibration data without source, 3 minutes without source, 8 detectors, scanning over 20 digipot values
2016-03-31 Added calibration run with 5 minute samples at 2 second chunks, for 20 digipot values (170-151)
2016-04-01 Added first calibration data with and without source
2016-04-26 Added VBIAS relay to steppercontroller, and fixed bug in digipot addressing for imagingarray
2016-04-26 added sample calibration data
2016-04-26 Added digipot calibration levels
2016-04-27 Added sample data with table/cube, sampled for 300s, 10 levels
2016-04-28 Additional sample data
2016-04-28 added summary_image.py tool, to convert from detector samples to a basic table summarizing the counts per (zLoc, rLoc), per detector, in counts per minute

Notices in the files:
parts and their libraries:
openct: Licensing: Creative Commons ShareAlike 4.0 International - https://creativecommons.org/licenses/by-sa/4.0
